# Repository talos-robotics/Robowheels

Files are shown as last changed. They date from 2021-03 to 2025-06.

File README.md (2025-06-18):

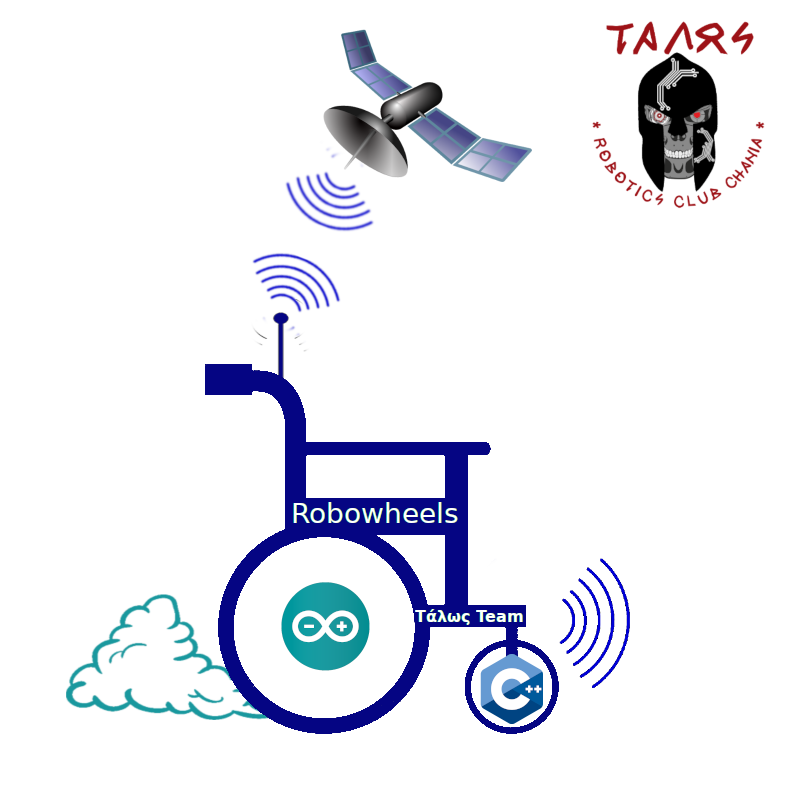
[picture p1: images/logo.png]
#   

<div style="background-color:#90EE90;">

# (The Robowheels project)

# Αυτοματοποιημένο αναπηρικό αμαξίδιο

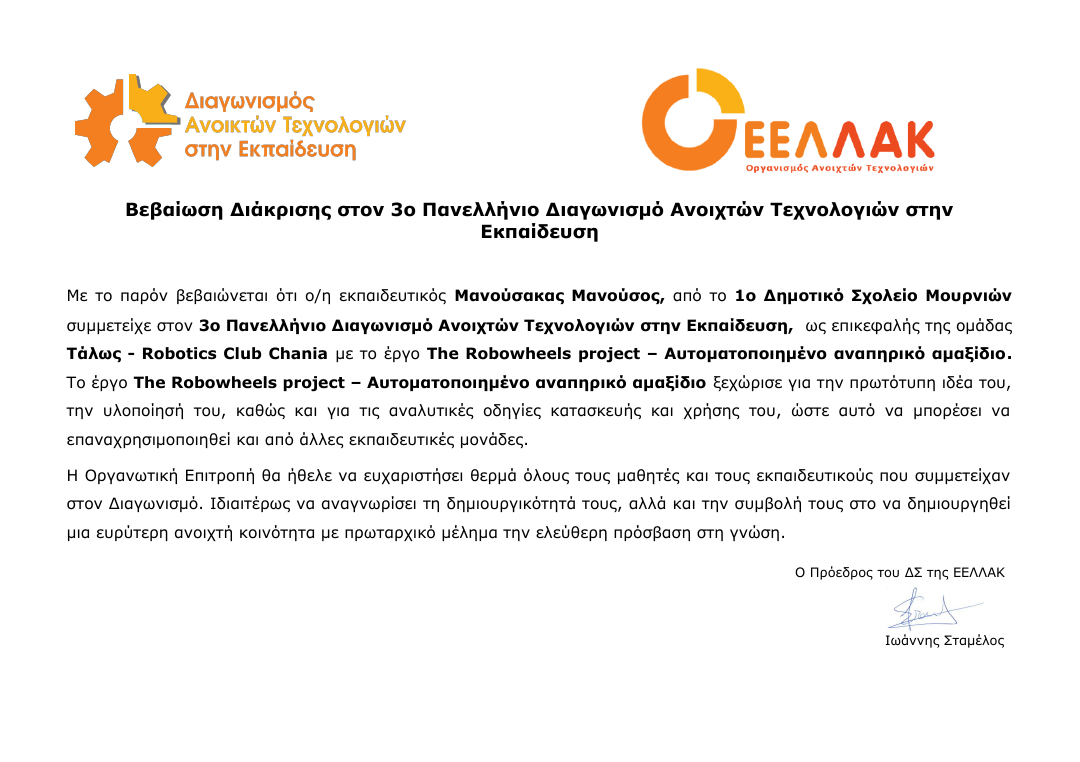
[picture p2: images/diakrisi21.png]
air


# Δημοσίευση στον τύπο
https://www.haniotika-nea.gr/ta-paidia-kainotomei/

</div>

<div style="text-align: left; ">

## <u>Συμμετέχοντες</u>

### Υπεύθυνος εκπαιδευτικός

Μανούσακας Μανούσος - Εκπαιδευτικός Πληροφορικής ΠΕ86

### Μαθητές

*   Αναστασάκης Ιωάννης
*   Ρουσιάκης Πέτρος
*   Στραβοπόδη Κωνσταντίνα

</div>

<div>

# <u>Γενικά στοιχεία σεναρίου</u>

## Σενάριο δραστηριότητας

Αριθμός μαθητών: 5  
Αριθμός Ομάδων: 2  
Αριθμός ατόμων ανά ομάδα: 2-3  
Είδος δραστηριότητας: Ομαδοσυνεργατική  
Ρόλοι: Δεν υπάρχουν διακριτοί ρόλοι στην ομάδα.  
Ηλικιακή ομάδα: 12-15  

## Φάση προετοιμασίας

Οι μαθητές θα πρέπει να:  
• Διερευνήσουν στο διαδίκτυο και να ανακαλύψουν τις ανάγκες των ατόμων με κινητικά προβλήματα.  
• Συντάξουν ένα έντυπο όπου θα περιγράφουν τις προδιαγραφές του project.  
• Να αναζητήσουν στο διαδίκτυο πληροφορίες για τους αισθητήρες που θα χρησιμοποιήσουμε.  

## Φάση σχεδιασμού

Οι μαθητές θα πρέπει να:  
• Να αναζητήσουν στο διαδίκτυο πληροφορίες για τη συνδεσμολογία των αισθητήρων με το Arduino.  
• Να αναζητήσουν στο διαδίκτυο πληροφορίες για τις προδιαγραφές των αισθητήρων.  
• Να δημιουργήσουν στο Fritzing τις παραπάνω συνδεσμολογίες.  

## Φάση υλοποίησης

Οι μαθητές θα πρέπει να:  
• Δημιουργήσουν τις φυσικές συνδέσεις των υλικών τους με τους αισθητήρες.  
• Να προγραμματίσουν το Arduino χρησιμοποιώντας το περιβάλλον Arduino IDE έτσι ώστε να παίρνουν τιμές από τους αισθητήρες.  

## Φάση Δοκιμών

Οι μαθητές θα πρέπει να:  
• Δοκιμάσουν τον εξοπλισμό τους και να επιβεβαιώσουν τη σωστή λειτουργία του.  

# Υλικά ηλεκτρονικά

<table style="width: 100%;" border="1">

<tbody>

<tr>

<th>ΠΟΣΟΤΗΤΑ</th>

<th>ΕΙΔΟΣ</th>

<th>ΚΟΣΤΟΣ</th>

<th>Σχόλια</th>

</tr>

<tr>

<td>1</td>

<td>ARDUINO UNO</td>

<td>25</td>

<td></td>

</tr>

<tr>

<td>2</td>

<td>GP2Y0A21YK0F Sharp IR Analog Distance Sensor</td>

<td>20</td>

<th>  
</th>

</tr>

<tr>

<td>1</td>

<td>Adafruit Επιταχυνσιόμετρο 3 Αξόνων ±2/4/8g @ 14-bit - MMA8451</td>

<td>8</td>

<th>  
</th>

</tr>

<tr>

<td>2</td>

<td>12V 35RPM JGY37-520 - 37mm Eccentric Large Torque Gear Motor Gearbox with Metal Gearbox</td>

<td>13</td>

<th>  
</th>

</tr>

<tr>

<td>1</td>

<td>Οδηγός για Βηματικό Κινητήρα L298N Dual H Bridge</td>

<td>4</td>

<th>  
</th>

</tr>

<tr>

<td>3</td>

<td>LM2596 Step Down Module DC 3V-40V to 5V 12V 3A Voltage Regulator</td>

<td>15</td>

<th>  
</th>

</tr>

<tr>

<td>1</td>

<td>Voice Recognition Module Rev3 Kit -Arduino Compatible</td>

<td>32</td>

<th>  
</th>

</tr>

<tr>

<td>1</td>

<td>SIM808 GPS GSM GPRS Bluetooth Module W/2.4G Antenna Replace SIM908 For Arduino</td>

<td>44</td>
<td>ΧΡΕΙΑΖΕΤΑΙ ΜΟΝΟ ΓΙΑ ΤΗΝ ΠΕΡΙΠΤΩΣΗ ΑΝΑΒΑΘΜΙΣΗΣ – ΕΠΕΚΤΑΣΗΣ. ΟΧΙ ΓΙΑ ΤΗΝ ΒΑΣΙΚΗ ΕΚΔΟΣΗ.</td>

<th>  
</th>

</tr>

<tr>

<td>2</td>

<td>Πυκνωτές >10μF</td>

<td>1</td>

<td></td>

</tr>

<tr>

<td>2</td>

<td>UPS BATTERY 12V 14AH MAX. 210A</td>

<td>20</td>

<td></td>

</tr>

<tr>

<td>  
</td>

<td>Σύνολο</td>

<td>170</td>

<th>  
</th>

</tr>

</tbody>

</table>

## Χρήσιμα αρχεία

<table style="width: 100%;" border="1">

<tbody>

<tr>

<th>ΠΕΡΙΓΡΑΦΗ</th>

<th>ΜΕΤΑΦΟΡΤΩΣΗ</th>

<th>ΣΧΟΛΙΑ</th>

</tr>

<tr>

<td>SharpIR Βιβλιοθήκη</td>

<td><a href="https://github.com/guillaume-rico/SharpIR.git">SharpIR Βιβλιοθήκη</a></td>

<td></td>

</tr>

<tr>

<td>Adafruit MMA8451 Βιβλιοθήκη</td>

<td><a href="https://github.com/adafruit/Adafruit_MMA8451_Library.git">Adafruit MMA8451 Βιβλιοθήκη</a></td>

<th>  
</th>

</tr>

<tr>

<td>Adafruit Sensor Βιβλιοθήκη</td>

<td><a href="https://github.com/adafruit/Adafruit_Sensor.git">Adafruit Sensor Βιβλιοθήκη</a></td>

<td></td>

</tr>

<tr>

<td>Voice Recognition Module οδηγός χρήσης</td>

<td><a href="images/VR3_manual.pdf">VR3_manual.pdf</a></td>

<td></td>

</tr>

<tr>

<td>Voice Recognition Module Βιβλιοθήκη</td>

<td><a href="https://www.google.com/url?q=https%3A%2F%2Fgithub.com%2Felechouse%2FVoiceRecognitionV3%2Farchive%2Fmaster.zip&sa=D&sntz=1&usg=AFQjCNE7a6-RkPLi9FMpjxIFqR-6OoMh5Q">VR3 library</a></td>

<td></td>

</tr>

<tr>

<td>L298N Βιβλιοθήκη</td>

<td><a href="https://downloads.arduino.cc/libraries/github.com/AndreaLombardo/L298N-2.0.2.zip?_gl=1*4jdbxj*_ga*MTg5MDYwNzAzMC4xNjMyNDIyNjU0*_ga_NEXN8H46L5*MTYzMjk5NjE0Mi42LjAuMTYzMjk5NjE0Mi4w">L298N</a></td>

<td></td>

</tr>

<tr>

<td></td>

<td></td>

<td></td>

</tr>

</tbody>

</table>

## Υλικά για την κατασκευή

<table style="width: 100%;" border="1">
<tbody>
<tr>
<th>ΠΟΣΟΤΗΤΑ</th>
<th>ΕΙΔΟΣ</th>
<th></th>
<th>Σχόλια</th>
</tr>
<tr>
<td style="text-align: center;">1</td>
<td>Ράβδος αλουμινίου 4cm x 2cm  Μήκος - 1m</td>
<td></td>
<td></td>
</tr>
<tr>
<td style="text-align: center;">2</td>
<td>Ράβδος αλουμινίου 4cm x 2cm  Μήκος - 40 cm</td>
<td></td>
<td></td>
</tr>
<tr>
<td style="text-align: center;">2</td>
<td>Βάση για μοτέρ 3d μοντέλο για εκτύπωση</td>
<td></td>
<td><a href="https://github.com/talos-robotics/Robowheels/blob/main/images/JGB37-520%20mount.STL">Κατεβάστε απο εδώ</a></td>
</tr>
<tr>
<td></td>
<td>Βίδες αυτοδιάτρητες  - διάφορα μεγέθη</td>
<td></td>
<td></td>
</tr>
<tr>
<td style="text-align: center;">2</td>
<td>Ασφάλειες μεταλλικές - κοπίλια</td>
<td></td>
<td></td>
</tr>
<tr>
<td style="text-align: center;">2</td>
<td>Ρόδες  με διάμετρο υποδοχής 6mm</td>
<td></td>
<td></td>
</tr>
<tr>
<td style="text-align: center;">1</td>
<td>Γωνιακό προφίλ αλουμινίου 40 cm</td>
<td></td>
<td></td>
</tr>
<tr>
<td style="text-align: center;">1</td>
<td>Μονοτική ταινία</td>
<td></td>
<td></td>
</tr>
<tr>
<td style="text-align: center;">2</td>
<td>Ράβδος αλουμινίου 4cm x 2cm  Μήκος - 20m</td>
<td></td>
<td></td>
</tr>
<tr>
<td style="text-align: center;">12</td>
<td>Βίδες Υ:2cm Π:4χιλ.</td>
<td></td>
<td></td>
</tr>
<tr>
<td style="text-align: center;"></td>
<td>Καλώδια 0.4 mm Διάφορα χρώμματα</td>
<td></td>
<td></td>
</tr>
<tr>
<td style="text-align: center;"></td>
<td>Κολλητήρι -  Καλάι</td>
<td></td>
<td></td>
</tr>
<tr>
<td style="text-align: center;"></td>
<td>Πιστόλι σιλικόνης - Ράβδοι συλικόνης</td>
<td></td>
<td></td>
</tr>
<tr>
<td style="text-align: center;"></td>
<td>Δραπανοκατσάβιδο μπαταρίας</td>
<td></td>
<td></td>
</tr>
<tr>
<td style="text-align: center;">2</td>
<td>Ροδάκια Επίπλων Περιστρεφόμενα</td>
<td></td>
<td></td>
</tr>
</tbody>
</table>

## Κατασκευή υποτιθέμενου αμαξιδίου ( εξομοιωτή )

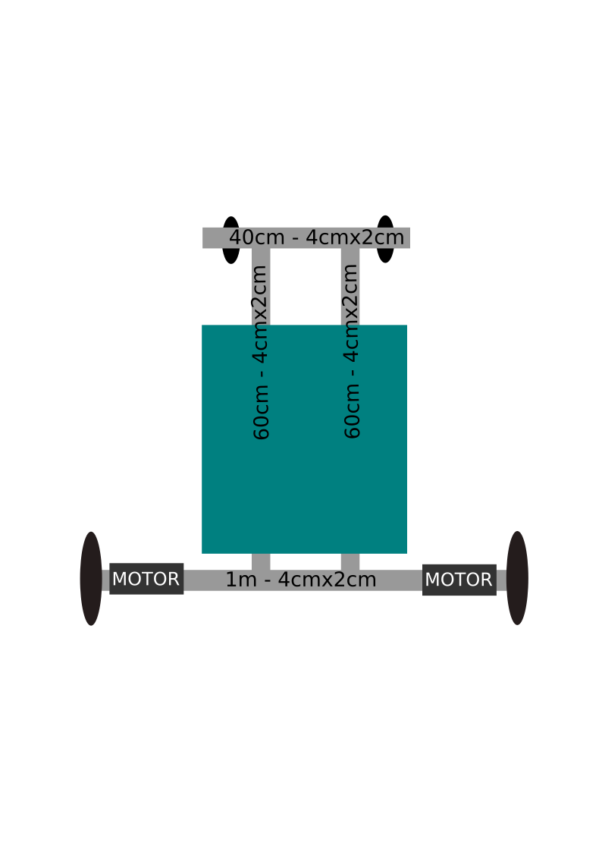
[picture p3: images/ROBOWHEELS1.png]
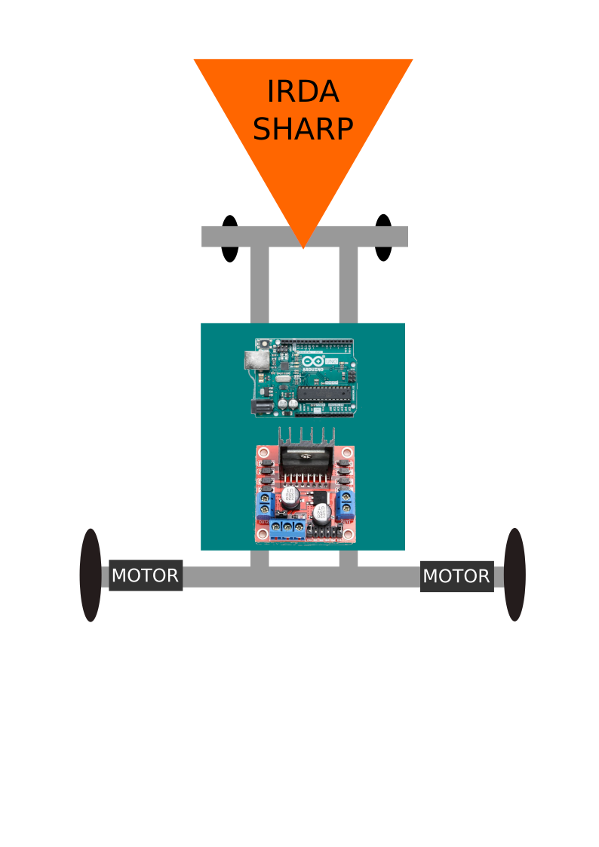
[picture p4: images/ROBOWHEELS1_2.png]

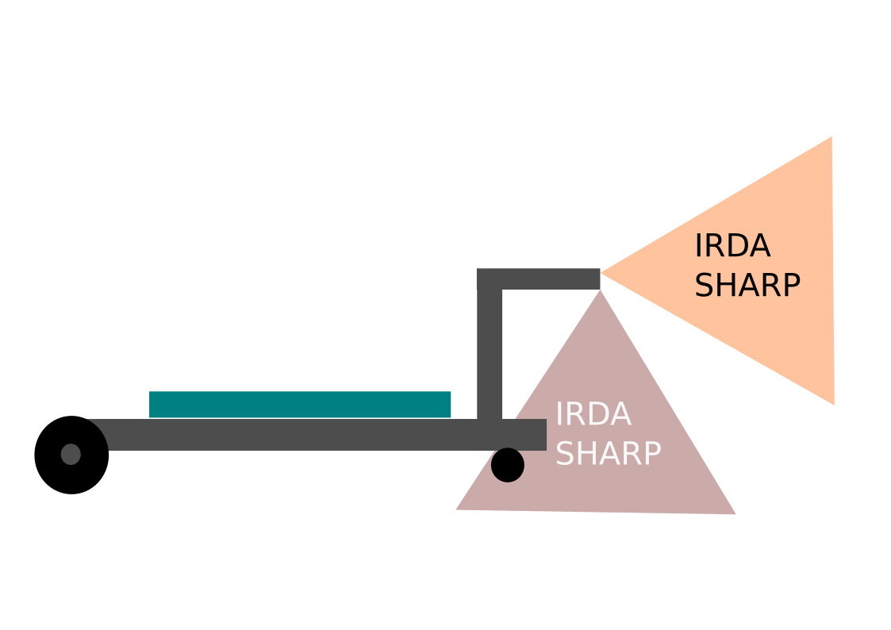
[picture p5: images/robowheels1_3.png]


## Προοπτική κατασκευής σε πραγματικό αμαξίδιο

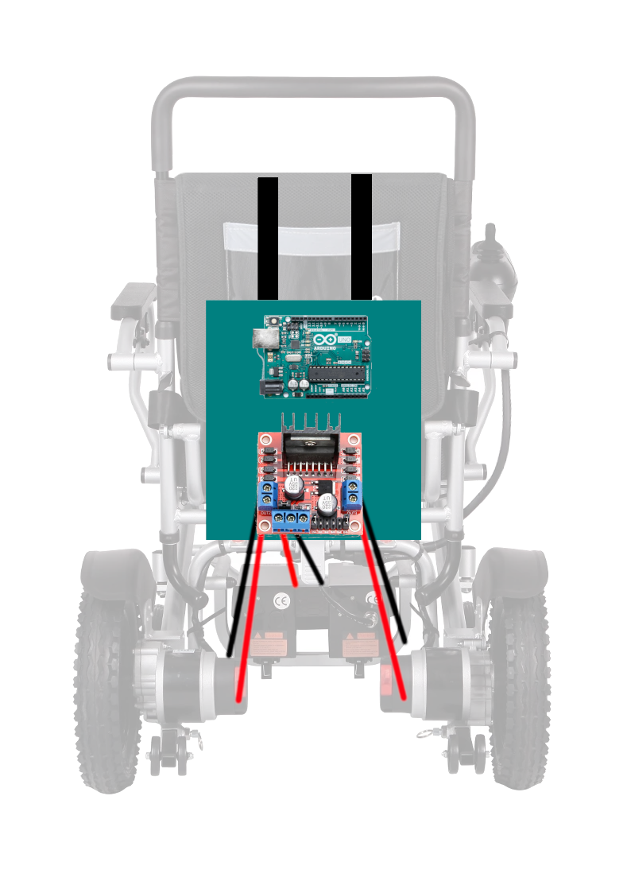
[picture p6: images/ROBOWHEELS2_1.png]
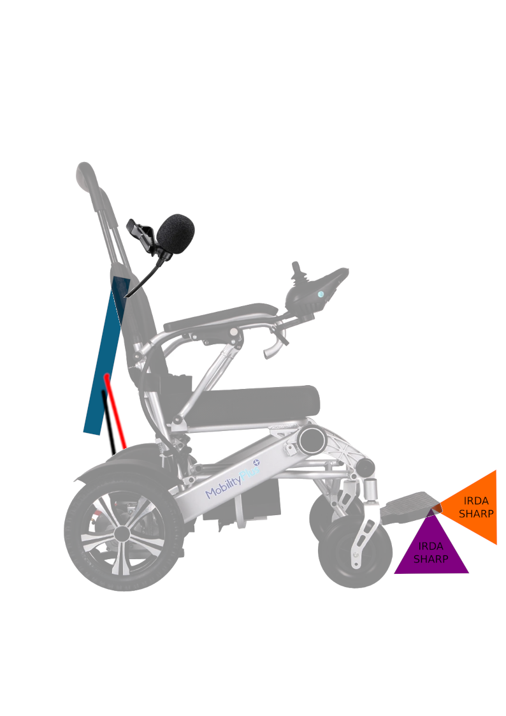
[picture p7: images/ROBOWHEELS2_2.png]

	
### <big>Αναλυτική περιγραφή</big>

Οι μαθητές αφού βρουν στοιχεία για την τετραπληγία και την παραπληγία 
θα μελετήσουν τις ανάγκες και τις λειτουργικές ικανότητες των ατόμων αυτών. 
Σκοπός είναι η δημιουργία ενός αυτοματοποιημένου οχήματος μετακίνησης που θα
προσαρμόζεται ανάλογα το μέλος του σώματος που θα είναι ικανός να θέσει σε
κίνηση ο χρήστης του. Θα παρέχει βασικές δικλείδες ασφαλείας για την ακινητοποίησή του.

<b>Ένα ηλεκτρικό αναπηρικό αμαξίδιο κοστίζει από 3000 ευρώ και πάνω. Θα ήταν αδύνατο να έχουμε στη διάθεση μας κάτι τέτοιο έτσι ώστε να το τροποποιήσουμε και να πειραματιστούμε.Άλλωστε ας μην ξεχνάμε πως ο διαγωνισμός έχει εκπαιδευτικό χαρακτήρα. Έτσι λοιπόν θα δημιουργήσουμε μια απλή κατασκευή που θα προσομοιώνει το αμαξίδιο και θα πειραματιστούμε πάνω σε αυτό. Οι αρχές λειτουργίας παραμένουν οι ίδιες.</b>
	
Ανάλογα την οικονομική και χρονική δυνατότητα που θα έχουμε, θα μπορούσε να προστεθεί 
και σύστημα εντοπισμού θέσης και επικοινωνίας που θα μπορεί να θέσει 
ο χρήστης σε λειτουργία σε περίπτωση κινδύνου.

Σκοπός και οφέλη

    • Ευαισθητοποίηση των μαθητών στο κοινωνικό θέμα της αναπηρίας.
    • Αναζήτηση λύσεων μετά από μελέτη προδιαγραφών και απαιτήσεων.
    • Εισαγωγή στην κατασκευή και λειτουργία βασικών ηλεκτρονικών κυκλωμάτων.
    • Εισαγωγή σε προγραμματιστικά περιβάλλοντα.
    • Εισαγωγή σε θέματα μηχανικής και κατασκευών.
    • Ομαδική δουλειά και συνεργασία.

</div>

<div>

# <u>Πλατφόρμες που χρησιμοποιήθηκαν</u>

Όλα τα διαδικτυακά εργαλεία που χρησιμοποιήσαμε ανήκουν στο Πανελλήνιο σχολικό δίκτυο.  

<small><small><font style="font-size: 24pt;" size="6"><small><small>**Πλατφόρμες εργασίας**</small></small></font></small></small>

<dl>

<dt><small><small><font style="font-size: 18pt;" size="5"><small><small>**Ηλεκτρονική τάξη:** https://eclass.sch.gr</small></small></font></small></small></dt>

<dt><small><small><font style="font-size: 18pt;" size="5"><small><small>**Πλατφόρμα τηλεδιασκέψεων:** cisco webex</small></small></font></small></small></dt>

<dt><small><small><font style="font-size: 18pt;" size="5"><small><small>**Ομαδοσυνεργατικά έγγραφα:** https://grafis.sch.gr</small></small></font></small></small></dt>

<dt><small><small><font style="font-size: 18pt;" size="5"><small><small>**Ηλεκτρονικό ταχυδρομείο:** https://webmail.sch.gr</small></small></font></small></small></dt>

<dt><small><small><font style="font-size: 18pt;" size="5"><small><small>**Υπηρεσία Επικοινωνίας:**</small></small></font><font style="font-size: 18pt;" size="5"><small> <small></small> </small></font><font style="font-size: 18pt;" size="5"><small><small>https://www.uc.sch.gr</small></small></font></small></small></dt>

</dl>

</div>

<div>

# <u>Εργαλεία ΕΛΛΑΚ που χρησιμοποιήθηκαν</u>

*   Libreoffice
*   Linux - Elementary OS
*   Arduino IDE
*   Fritzing

</div>

<div>

# <u>Πληροφορίες για το υλικό</u>

### Αισθητήρας GP2Y0A21 IRDA

<br />

Οι αισθητήρες απόστασης Sharp είναι μια δημοφιλής επιλογή για πολλά έργα που απαιτούν ακριβείς μετρήσεις απόστασης. 

Αυτός ο αισθητήρας υπερύθρων είναι απο τους πιο οικονομικούς, ωστόσο παρέχει πολύ καλύτερη απόδοση από άλλες εναλλακτικές λύσεις IR.
Η διασύνδεση με τους περισσότερους μικροελεγκτές είναι απλή.
Το εύρος ανίχνευσης αυτής της έκδοσης είναι περίπου 10 cm έως 80 cm (4 ″ έως 32).

Το GP2Y0A21 χρησιμοποιεί υποδοχή 3 ακίδων.Αυτά τα καλώδια έχουν συνδετήρες JST 3 ακίδων στο ένα άκρο και διατίθενται με προ-πτυχωμένες αρσενικές ακίδες,
στο άλλο άκρο. 
Είναι επίσης δυνατή η συγκόλληση τριών καλωδίων στον αισθητήρα όπου είναι τοποθετημένες οι ακίδες σύνδεσης 

	Κόκκινο --> 5V
	Μαύρο --> GND
	Κίτρινο --> DATA (Αναλογικό)

### Αισθητήρας Adafruit Επιταχυνσιόμετρο 3 Αξόνων ±2/4/8g @ 14-bit - MMA8451

<br />

Το MMA8451 είναι ένα μικροσκοπικό επιταχυνσιόμετρο από την Freescale, η οποία είναι (πλέον) αυθεντία στο παιχνίδι του σχεδιασμού επιταχυνσιόμετρων.
Έχει σχεδιαστεί για χρήση σε τηλέφωνα, tablet, έξυπνα ρολόγια και άλλα, αλλά λειτουργεί εξίσου καλά και στο έργο σας Arduino.
Από την οικογένεια MMA8451/MMA8452/MMA8453, ο MMA8451 είναι ο πιο ακριβής με ενσωματωμένο ADC 14-bit.
Το επιταχυνσιόμετρο διαθέτει επίσης ενσωματωμένη ανίχνευση κλίσης/προσανατολισμού, ώστε να μπορεί να σας πει αν το έργο σας βρίσκεται σε οριζόντια ή κατακόρυφη θέση
και αν έχει κλίση προς τα εμπρός ή προς τα πίσω.

Τυπική Τάση Εισόδου:
    3VDC
    5VDC
Ρεύμα Λειτουργίας: 165uA
Διασύνδεση:Ψηφιακή 
Πρωτόκολλο Eπικοινωνίας:I2C

 **Αρχή λειτουργίας επιταχυνσιόμετρου.**

IMAGE ALT TEXT HERE (https://www.youtube.com/embed/To7JagpPDwY)

### Κινητήρας dc 12V 35RPM JGY37-520 - 37mm Eccentric Large Torque Gear Motor Gearbox with Metal Gearbox



Οι Κινητήρες DC είναι συνεχείς ενεργοποιητές που μετατρέπουν την ηλεκτρική ενέργεια σε μηχανική ενέργεια. Ο κινητήρας DC επιτυγχάνει αυτό με τη δημιουργία μιας συνεχούς γωνιακής περιστροφής που μπορεί να χρησιμοποιηθεί για την περιστροφή αντλιών, ανεμιστήρων, συμπιεστών, τροχών κλπ. Ο κινητήρας DC ή κινητήρας συνεχούς ρεύματος για να του δώσουμε τον πλήρη τίτλο του είναι ο συνηθέστερα χρησιμοποιούμενος κινητήρας για την παραγωγή συνεχούς κίνηση και της οποίας η ταχύτητα περιστροφής μπορεί εύκολα να ελεγχθεί, καθιστώντας τους ιδανικά για χρήση σε διάφορες εφαρμογές. Ένας ηλεκτροκινητήρας συνεχούς ρεύματος αποτελείται από δύο μέρη, έναν "στάτορα" που είναι το σταθερό τμήμα και έναν "περιστροφέα" που είναι το περιστρεφόμενο τμήμα. Οι κινητήρες DC έχουν σχεδόν γραμμικά χαρακτηριστικά με την ταχύτητα περιστροφής τους να καθορίζεται από την εφαρμοζόμενη τάση συνεχούς ρεύματος και η ροπή εξόδου τους να καθορίζεται από το ρεύμα που ρέει μέσω των περιελίξεων του κινητήρα. Η ταχύτητα περιστροφής κάθε κινητήρα DC μπορεί να ποικίλει από μερικές περιστροφές ανά λεπτό (σ.α.λ.) σε πολλές χιλιάδες στροφές ανά λεπτό, καθιστώντας τις κατάλληλες για ηλεκτρονικές, αυτοκινητοβιομηχανικές ή ρομποτικές εφαρμογές. Συνδυάζοντας τους με κιβώτια ταχυτήτων (Gearbox), η ταχύτητα εξόδου τους μπορεί να μειωθεί, ενώ παράλληλα αυξάνει την ισχύ ροπής του κινητήρα σε υψηλή ταχύτητα.

### Οδηγός για Βηματικό Κινητήρα L298N Dual H Bridge



Το L298N είναι ένας οδηγός για κινητήρες συνεχούς ρεύματος. Με αυτό το πλακετάκι μπορείς να δώσεις κίνηση στους κινητήρες σου, υποστηρίζει έως δύο κινητήρες μέγιστης ισχύς 2A ανά κινητήρα. Μικρός σε μέγεθος για εφαρμογή σε πλήθος κατασκευών, διαθέτει κλέμες για την σύνδεση των κινητήρων και του ρεύματος. Έχεις την δυνατότητα να το χρησιμοποιήσεις και σε μεγαλύτερο εύρος εφαρμογών εκτός από κινητήρες, όπως ρελέ, solenoids, DC ή Stepper κινητήρες.

ΧΑΡΑΚΤΗΡΙΣΤΙΚΑ
Max. Current per Channel: 2A
Τύπος Οδηγού: DC Motor Stepper

ΕΠΙΠΛΕΟΝ ΧΑΡΑΚΤΗΡΙΣΤΙΚΑ

Driver: L298N Dual H Bridge DC Motor Driver IC
Motor Power Supply Vs: +5 V to +35 V
Max average current: 2A
Peak current Io: 3A
Logic Level Power Vss: +5 V ~ +7 V (Onboard 5V Regulator can be used if Motor Power is > 7.0V)
Logic level power: 0 - 36mA
Logic signal input range: [ Low:-0.3V ≤ Vin ≤ 1.5V] [ High: 2.3V ≤ Vin ≤ Vss]
Maximum power dissipation: 20W (when the temperature T = 75 ℃)

### Μετατροπέας DC-DC Step-Down 1.3-35V 3A



Πρόκειται για ένα DC Adjustable Step Down Module που μπορεί να χρησιμοποιηθεί 
για την επίτευξη εύρους ρυθμιζόμενης τάσης εξόδου 1.3V-35V με βάση το LM2596S.
Περιλαμβάνει LC Ripple Filtering για ομαλότερη τάση εξόδου.

ΧΑΡΑΚΤΗΡΙΣΤΙΚΑ
Τάση Εισόδου: 3.2-40Volt
Τάση Εξόδου: 1.3-35Volt
Ένταση Εξόδου: 3Amp
ΕΠΙΠΛΕΟΝ ΧΑΡΑΚΤΗΡΙΣΤΙΚΑ

    Input voltage 3.2V - 40V
    Output voltage 1.3V - 35V
    Output current 3A (max)
    Conversion efficiency of 92% (maximum)
    Output ripple <30mV
    Switching frequency 65KHz
    Operating temperature -45 ℃ ~ +85 ℃

### Αισθητήρας Αναγνώρισης Φωνής



Το Voice Recognition Module είναι μια εύχρηστη μονάδα αναγνώρισης ομιλίας που μπορεί εύκολα να διασυνδεθεί με το Arduino.
Υποστηρίζει συνολικά έως και 80 φωνητικές εντολές.
Μέγιστες 7 φωνητικές εντολές θα μπορούσαν να λειτουργήσουν ταυτόχρονα. Κάθε ήχος θα μπορούσε να εκπαιδευτεί ως εντολή.
Οι χρήστες πρέπει πρώτα να εκπαιδεύσουν τη μονάδα πριν την αφήσουν να αναγνωρίσει οποιαδήποτε φωνητική εντολή.

ΧΑΡΑΚΤΗΡΙΣΤΙΚΑ
Τύπος Αισθητήρα:

    Ήχου

Τυπική Τάση Εισόδου:

    5VDC
    5.5VDC

Ρεύμα Λειτουργίας: 40mA
Διασύνδεση:

    Ψηφιακή 

Πρωτόκολλο Eπικοινωνίας:

    UART

ΕΠΙΠΛΕΟΝ ΧΑΡΑΚΤΗΡΙΣΤΙΚΑ

    Voltage: 4.5-5.5V
    Current: <40mA
    Digital Interface: 5V TTL level for UART interface and GPIO
    Analog Interface: 3.5mm mono-channel microphone connector + microphone pin interface
    Recognition accuracy: 99% (under ideal environment)

### Waveshare GSM/GPRS/GPS Shield SIM808 - Χρειάζεται μόνο για την περίπτωση αναβάθμισης - επέκτασης. Όχι για αυτή την βασική έκδοση. Θα δημιουργηθεί σαν ξεχωριστό project στο μέλλον



Το GSM/GPRS/GPS Shield (B) είναι μια ασπίδα Arduino που βασίζεται στη μονάδα τεσσάρων ζωνών GSM/GPRS/GPS SIM808.

ΧΑΡΑΚΤΗΡΙΣΤΙΚΑ
Τυπος Shield:

    GPRS/GSM
    GPS

ΕΠΙΠΛΕΟΝ ΧΑΡΑΚΤΗΡΙΣΤΙΚΑ

    Arduino connectivity, compatible with UNO, Leonardo, NUCLEO, XNUCLEO
    Onboard USB TO UART converter CP2102 for UART debugging
    5 x LEDs for indicating the module working status
    Onboard voltage level converter, supports both 3.3V and 5V systems
    SIM card slot for 1.8V/3V SIM card
    Baudrate auto detection (1200bps ~115200bps)
    Bluetooth 3.0， supports data transferring through Bluetooth
    RTC with power supply interface
    Firmware upgradable via USB
    Control via AT commands (3GPP TS 27.007,27.005, and SIMCOM enhanced AT Commands)
    Supports SIM application toolkit: GSM 11.14 Release 99
    Operating voltage: 6 ~ 12V
    Operation temperature: -40 °C ~ +85 °C
    Storage temperature: -45 °C ~ +90 °C

ΔΥΝΑΤΟΤΗΤΕΣ

GSM/GPRS

    Band
        GSM 850/EGSM 900/DCS 1800/PCS 1900 MHz
        Quad-band auto search
        Compliant to GSM phase 2/2+
    Emitting power
        Class 4 (2W @ GSM 850/EGSM 900 MHz)
        Class 1 (1W @ DCS 1800/PCS 1900 MHz)
    GPRS connectivity
        GPRS multi-slot class 12 (default)
        GPRS multi-slot class 1~12 (configurable)
    GPRS data feature
        Downlink speed: max 85.6kbps
        Uplink speed: max 85.6kbps
        Coding schemes: CS-1\CS-2\CS-3\CS-4
        Supports PAP (Password Authentication Protocol) for PPP connection
        Embedded TCP/IP protocol
        Supports PBCCH
        Supports CSD transmission speed: 2.4/4.8/9.6/14.4 kbps
        Supports USSD
    SMS
        Supports: MT/MO/CB/Text/PDU mode
        SMS storage: SIM card
    Audio
        Voice encode/decode mode: Half Rate\Full Rate\Enhanced Full Rate\Adaptive muti rate
        Supports echo cancellation
        Supports noise reduction

GPS

    Receiver type
        22 tracking channels
        66 acquisition channels
        GPS L1 C/A code
    Sensitivity
        Tracking: -165 dBm
        Cold starts : -148 dBm
    Time-To-First-Fix
        Cold starts : 30s (typ.)
        Hot starts : < 1s
        Warm starts: 28s
    Accuracy
        Horizontal position : <2.5m CEP

</div>

<div style="text-align: center; text-decoration:">

# Συνδεσμολογία Υλικού

<div style="text-align: left; font-size: 12pt; background-color:yellow">

**<u>ΠΕΡΙΓΡΑΦΗ ΛΕΙΤΟΥΡΓΙΑΣ - Με τη χρήση ΜΜΑ8451</u>**

Στη συγκεκριμένη εκδοχή χρησιμοποιούμε ένα γυροσκοπικό αισθητήρα τον οποίο τον προσαρμόζουμε στο μέλος του σώματος που μπορεί το άτομο με τετραπληγία να κινήσει. Ανάλογα την κλήση που δέχεται ο γυροσκοπικός αισθητήρας από τον χρήστη εκτελεί τις αντίστοιχες κινήσεις. Όταν τον γείρει μπροστά τα μοτέρ εκτελούν εμπρόσθια κίνηση. Όταν τον γείρει πίσω τα μοτέρ εκτελούν κίνηση προς τα πίσω. Αντίστοιχα όταν τον γείρει δεξιά ή αριστερά τα μοτέρ εκτελούν τις αντίστοιχες κινήσεις.

Αυτός ο τρόπος έχει σημαντικά πλεονεκτήματα. Ένας άνθρωπος με κινητικές δυσκολίες μπορεί να έχει πολλές ιδιαιτερότητες στο μέλος του σώματος που θα θέτει το όχημα σε κίνηση.
Για παράδειγμα αν περιστρέφει τον αισθητήρα με το κεφάλι του, η κίνηση που κάνει δεξιά ίσως είναι μικρότερη της κίνησης που κάνει αριστερά, Με αυτό τον αισθητήρα μπορούμε να ρυθμίσουμε την ευαισθησία της κάθε κίνησης κατά το δοκούν.

</div>

#### Κατεβάστε τον κώδικα

<a href="/files/robowheelsDC.ino">Κώδικας με τον αισθητήρα MMA8451</a>

</div>

<div style="text-align: center; text-decoration:">

<div style="text-align: left; font-size: 12pt; background-color:yellow">

**<u>ΠΕΡΙΓΡΑΦΗ ΛΕΙΤΟΥΡΓΙΑΣ - Με τη χρήση Αναγνώρισης φωνής</u>**

Στη συγκεκριμένη εκδοχή χρησιμοποιούμε μία μονάδα αναγνώρισης φωνής και με φωνητικές εντολές, οι οποίες
έχουν προγραμματιστεί εκ των προτέρων, μπορεί να θέσει σε κίνηση ο χρήστης τα μοτέρ.
Για παράδειγμα θα μπορούσε να πει τη λέξη μπροστά και τα μοτέρ να εκτελέσουν εμπρόσθια κίνηση.
Θα μπορούσε να πει τη λέξη δεξιά και τα μοτέρ να εκτελέσουν δεξιά στροφή.
Θα μπορούσε να πει την λέξη stop για να μπορέσει να τερματίσει τη λειτουργία του μοτέρ.
Ένα πλεονέκτημα της συγκεκριμένης μονάδας αναγνώρισης φωνής, είναι ότι είναι ανεξάρτητη γλώσσας και χροιάς.
Μπορεί και συγκρίνει τους φθόγγους με αυτό που έχουμε καταγράψει αρχικά. 
Επίσης κάποιοι συνάνθρωποί μας με δυσκολία στην ομιλία ίσως μπορούν να προφέρουν μόνο ήχους. Είναι σε θέση η μονάδα αυτή να τους κατανοήσει. 
Μια πολύ θετική παράμετρος.
Ενα βασικό μειονέκτημα της πολύ σημαντικό είναι ότι επηρεάζεται αρνητικά από τους περιβάλλοντες ήχους με
αποτέλεσμα να μην μπορεί να γίνει σωστά η αναγνώριση.

<a href="/files/robowheels_voiceDC.ino">Κώδικας με τον αισθητήρα voice</a>
	
</div>

#### Συνδεσμολογία

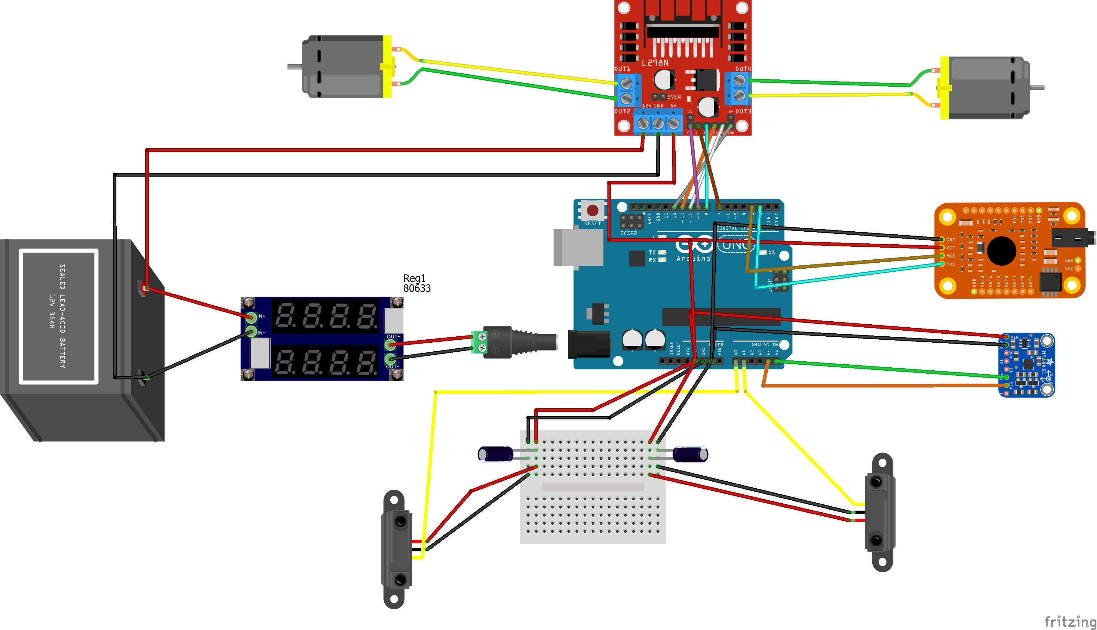
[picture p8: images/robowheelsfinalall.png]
  

#### Εκπαιδεύστε το module σας

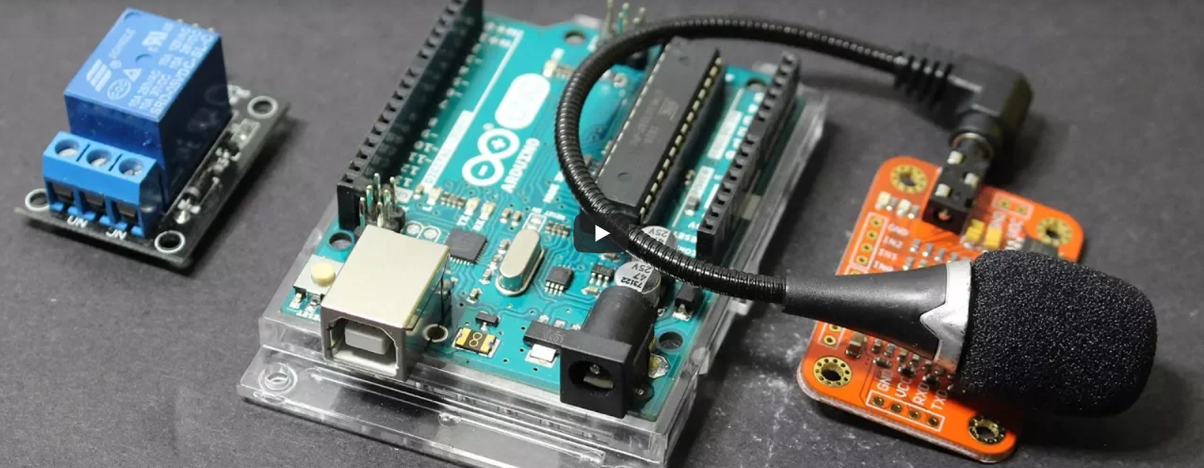
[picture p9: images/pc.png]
IMAGE ALT TEXT HERE (https://www.youtube.com/embed/bTrv1nv3oSA)


</div>

<div>

# <u><center>Στάδια εξέλιξης - Τελικό πρωτότυπο</center></u>

## Βίντεο - Παρουσίαση
IMAGE ALT TEXT HERE (https://www.youtube.com/embed/V4w2R3GzmRQ)

## Φωτογραφίες
<table style="width: 100%;" border="1">
<tbody>
<tr align="center">
<td></td>
<td></td>
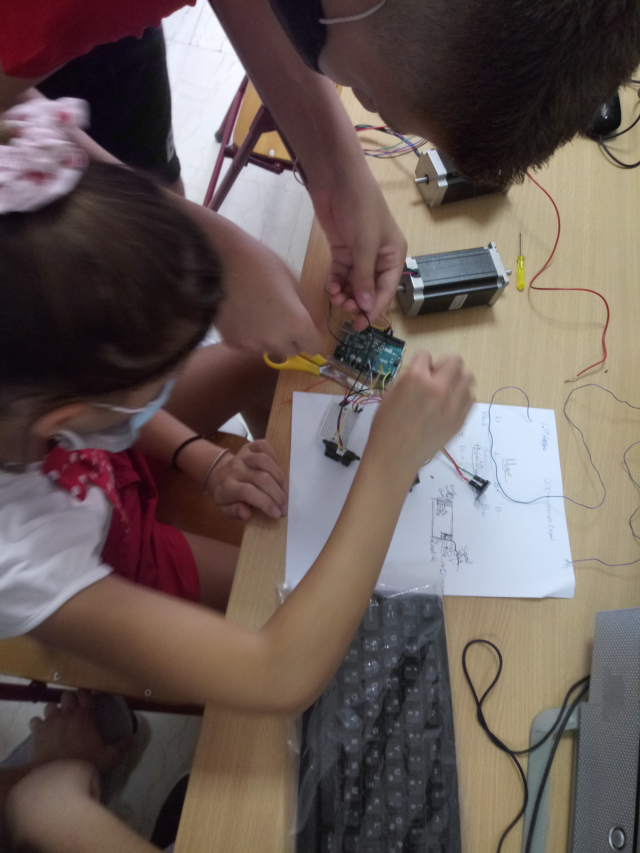
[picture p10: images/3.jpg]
<td></td>
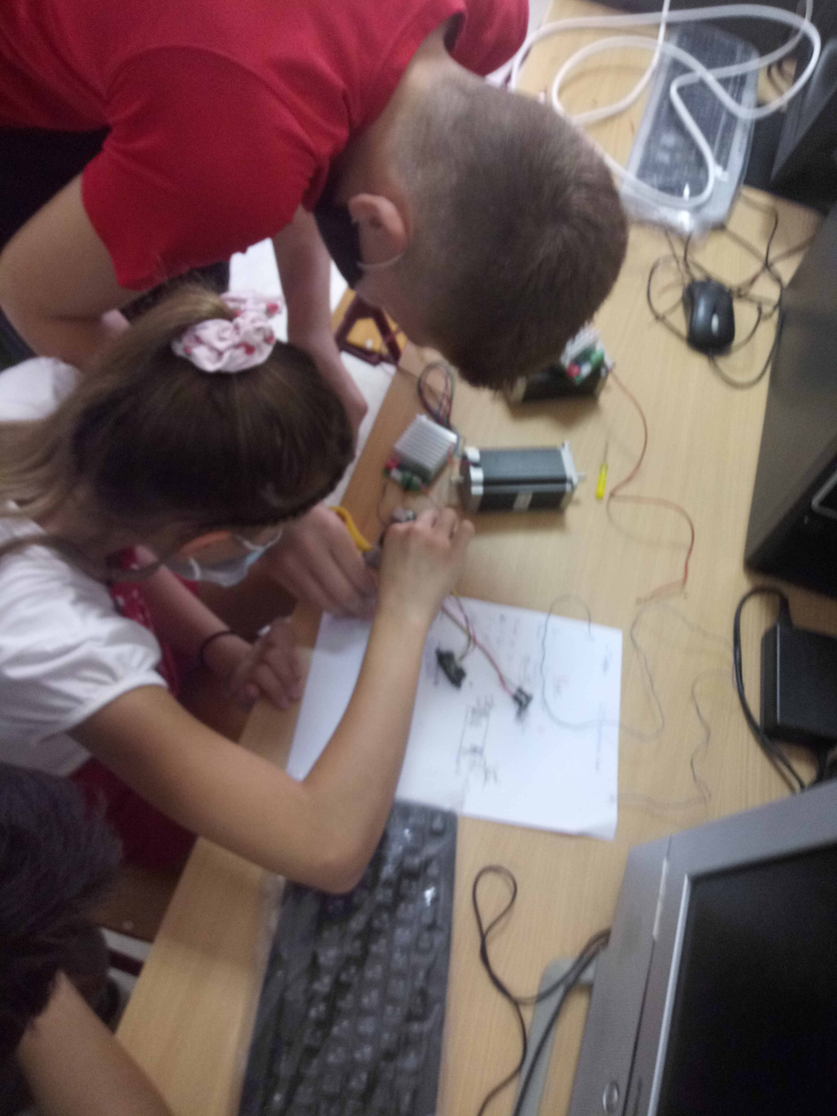
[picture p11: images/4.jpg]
<td></td>
</tr>
<tr align="center">
<td></td>
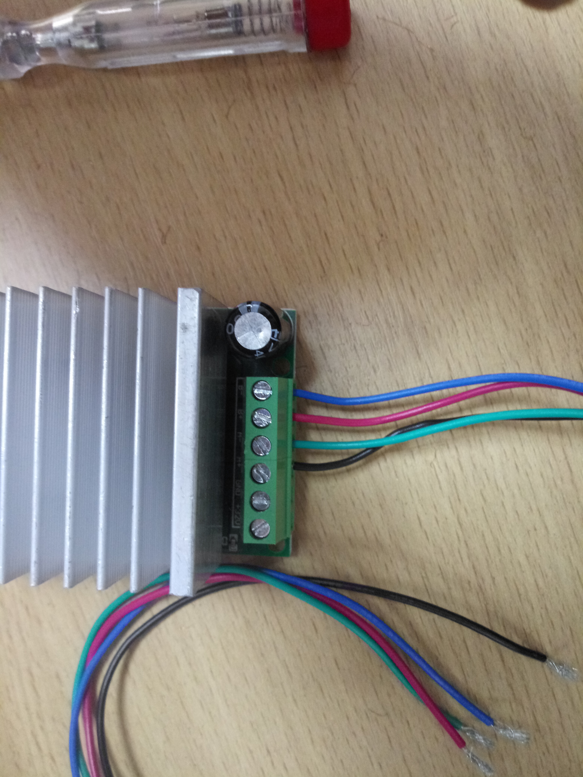
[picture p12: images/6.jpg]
<td></td>
<td></td>
<td></td>
</tr>
<tr align="center">
<td></td>
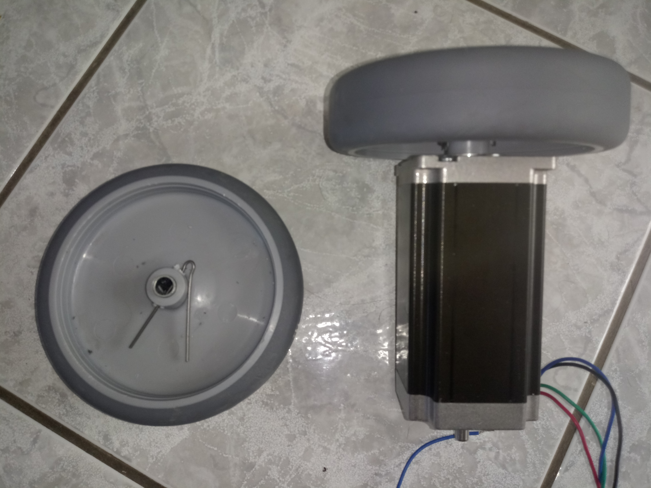
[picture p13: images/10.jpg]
<td></td>
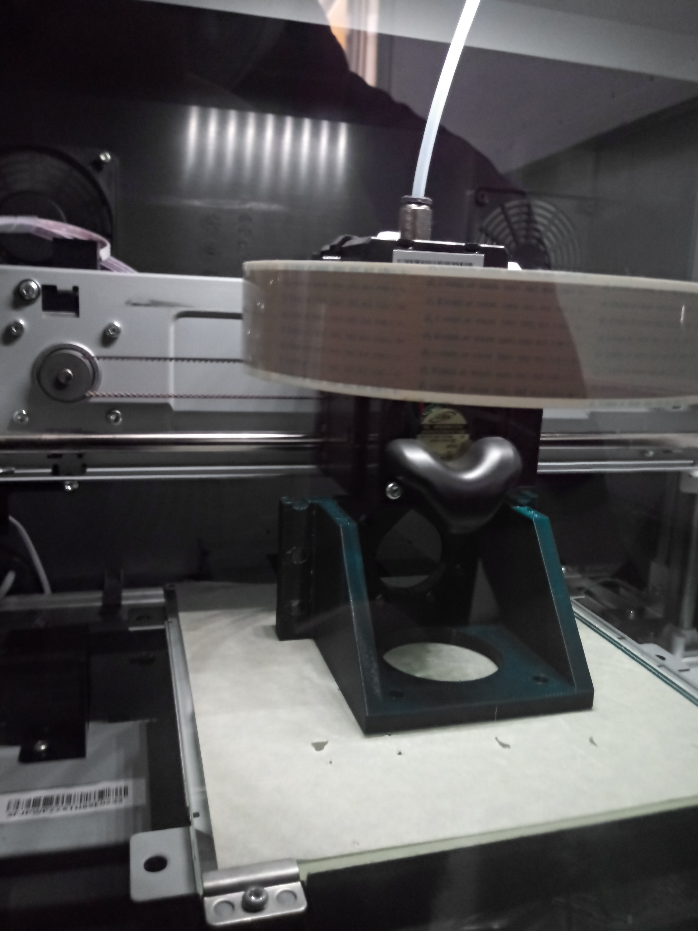
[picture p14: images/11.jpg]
<td></td>
<td></td>
</tr>
<tr align="center">
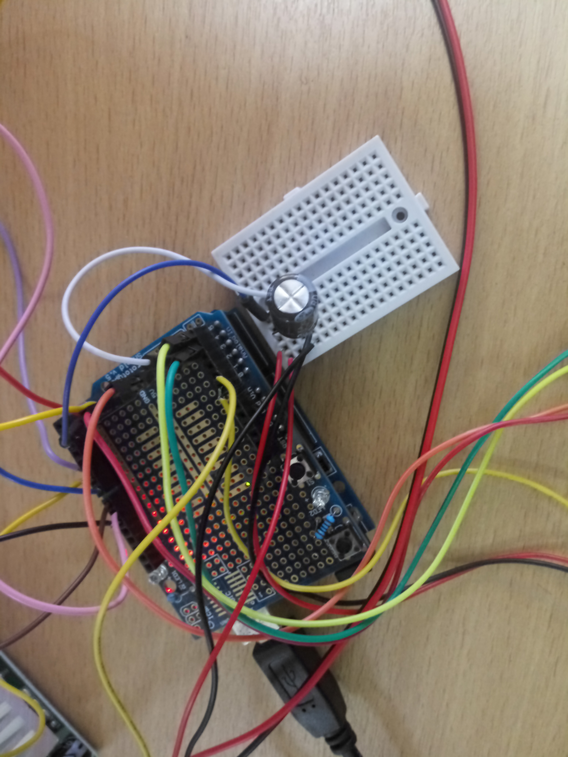
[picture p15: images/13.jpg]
<td></td>
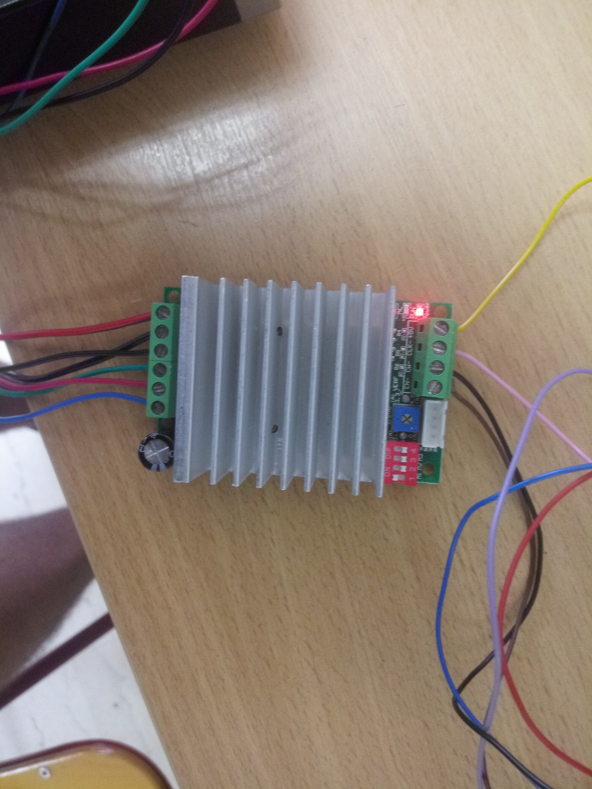
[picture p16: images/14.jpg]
<td></td>
<td></td>
<td></td>
</tr>
<tr align="center">
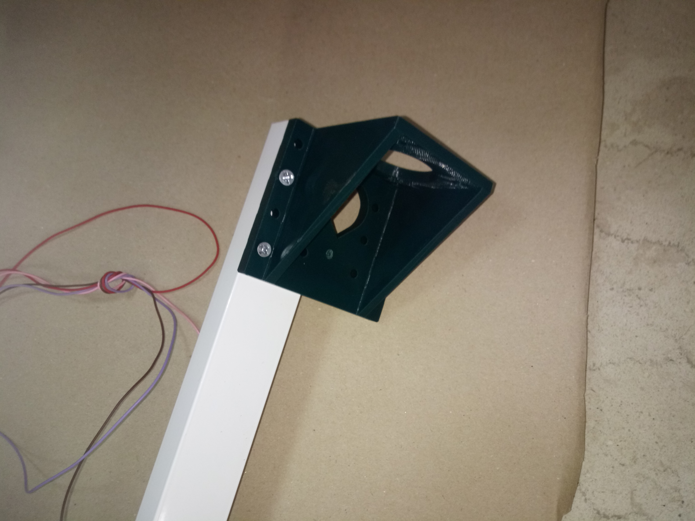
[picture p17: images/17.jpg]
<td></td>
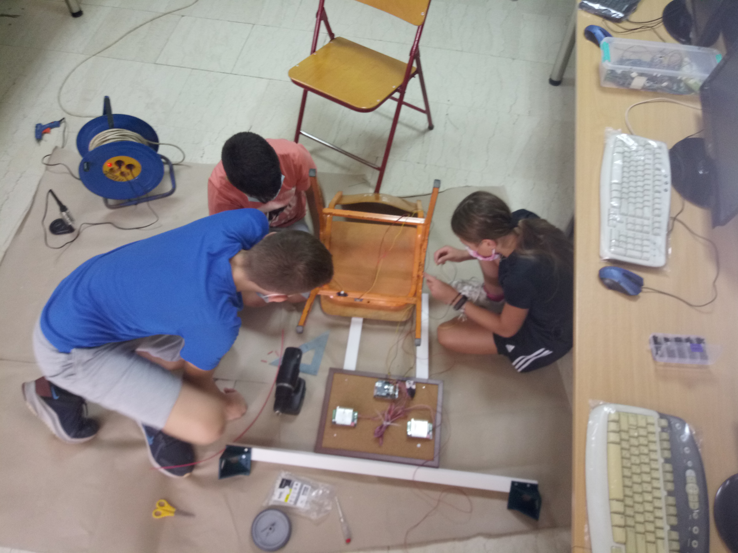
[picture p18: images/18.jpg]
<td></td>
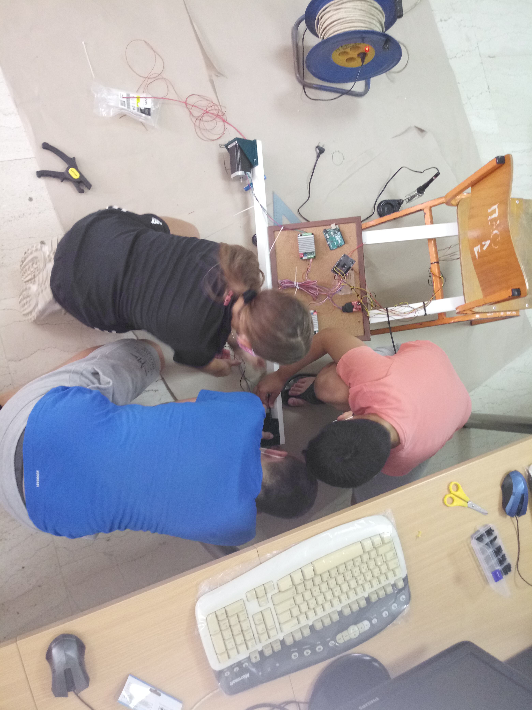
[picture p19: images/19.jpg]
<td></td>
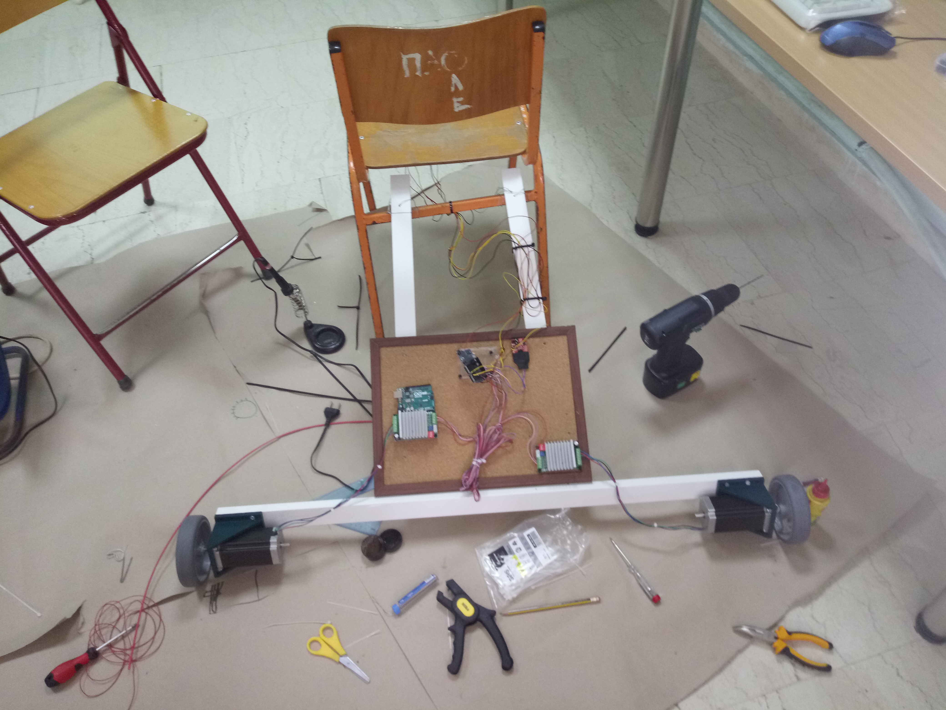
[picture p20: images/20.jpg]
<td></td>
</tr>
<tr align="center">
<td></td>
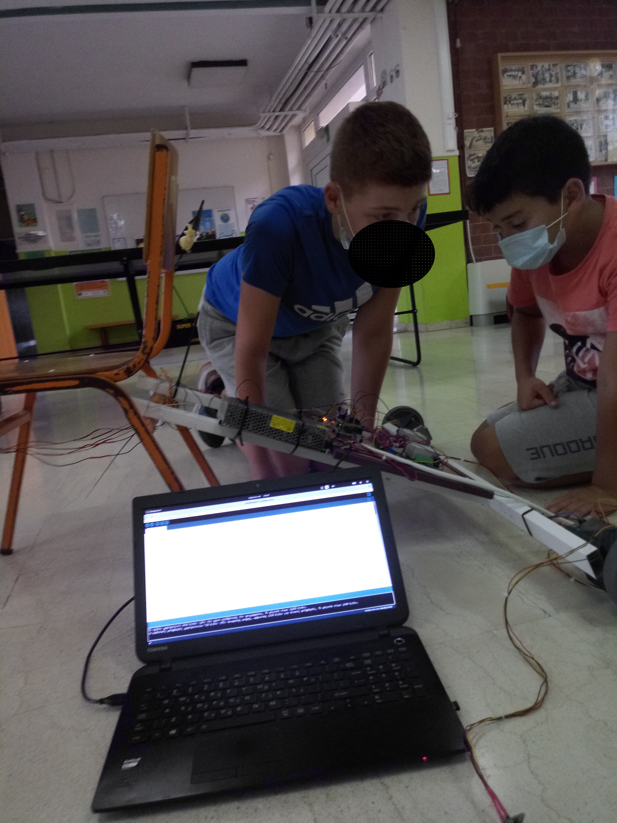
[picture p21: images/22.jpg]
<td></td>
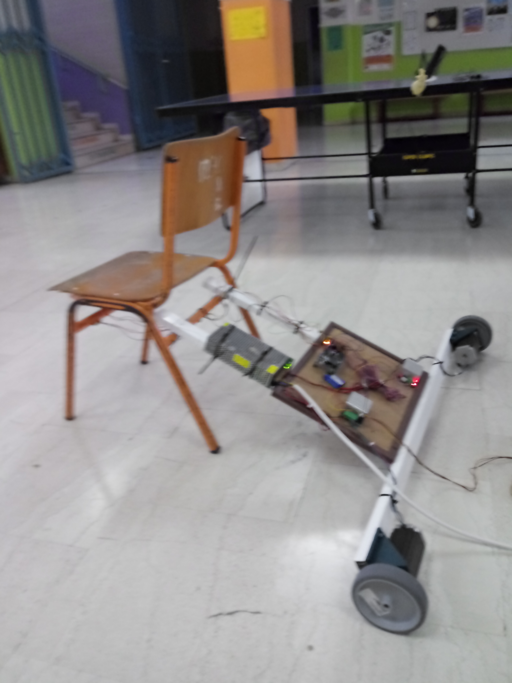
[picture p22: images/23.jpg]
<td></td>
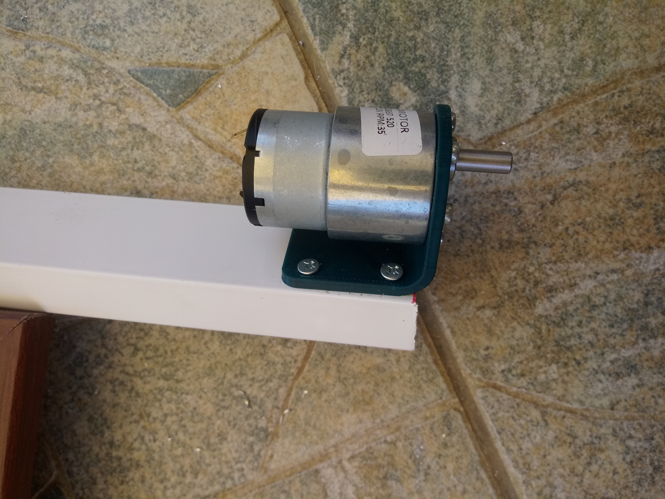
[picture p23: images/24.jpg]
<td></td>
</tr>
<tr align="center">
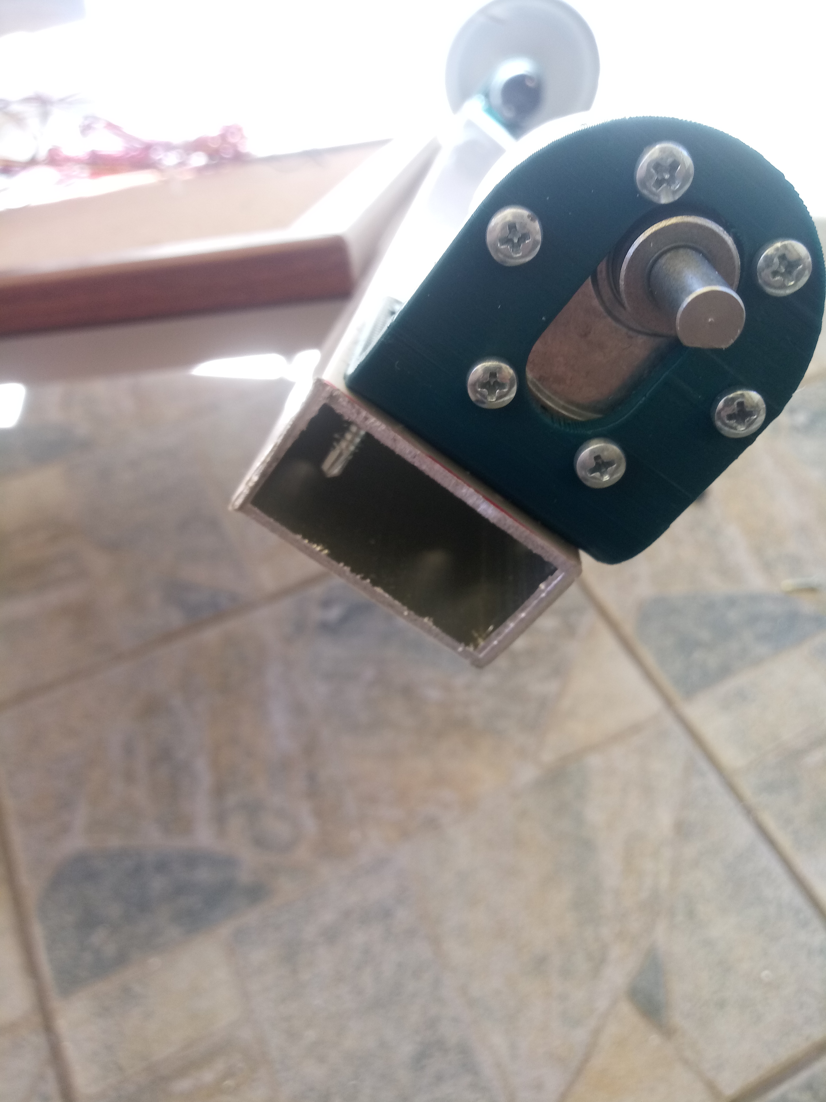
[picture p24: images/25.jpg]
<td></td>
<td></td>
<td></td>
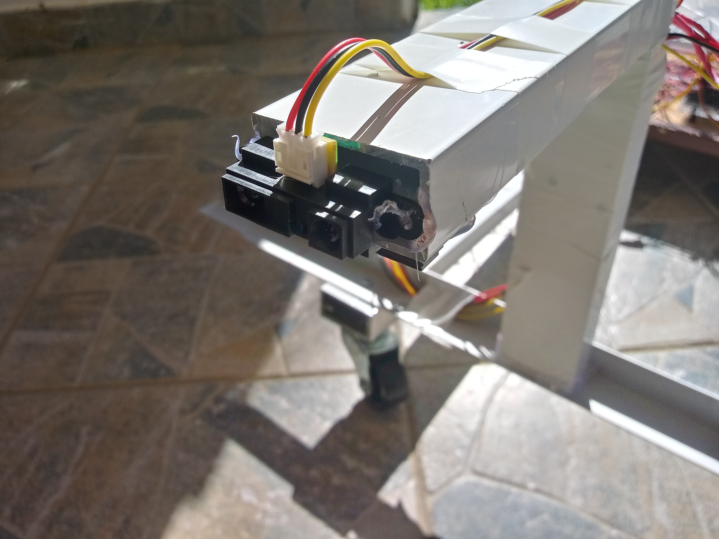
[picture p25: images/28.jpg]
<td></td>
</tr>
<tr align="center">
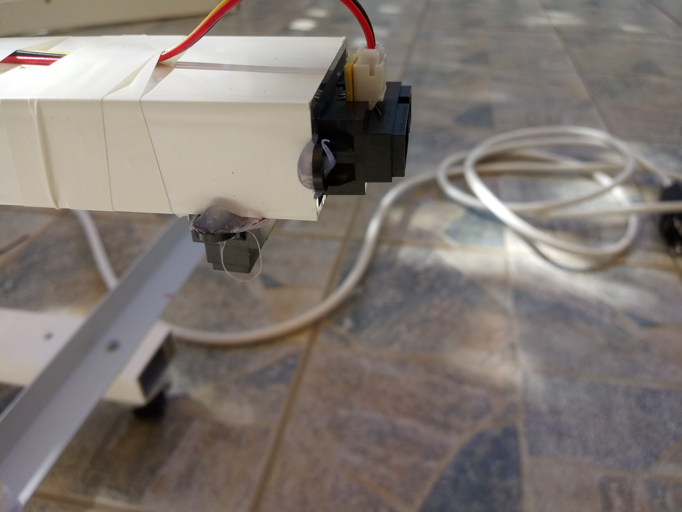
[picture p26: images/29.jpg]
<td></td>
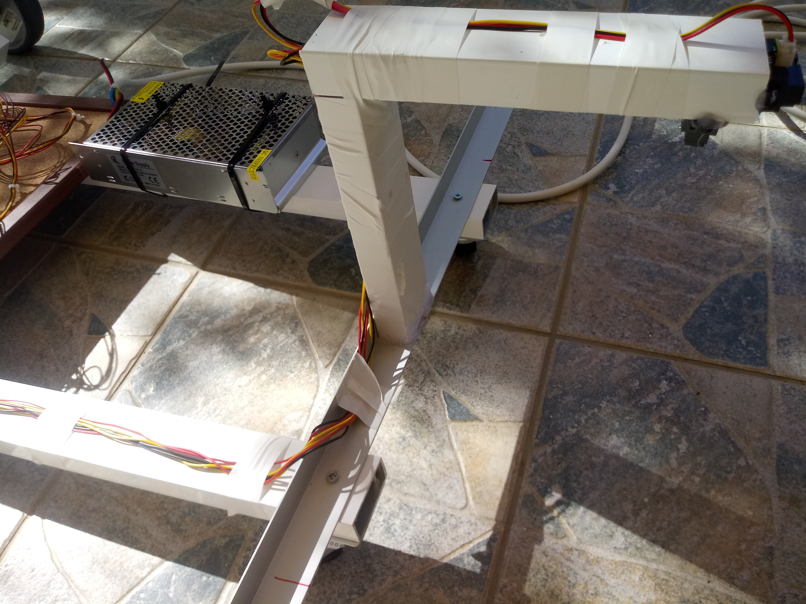
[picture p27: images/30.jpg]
<td></td>
<td></td>
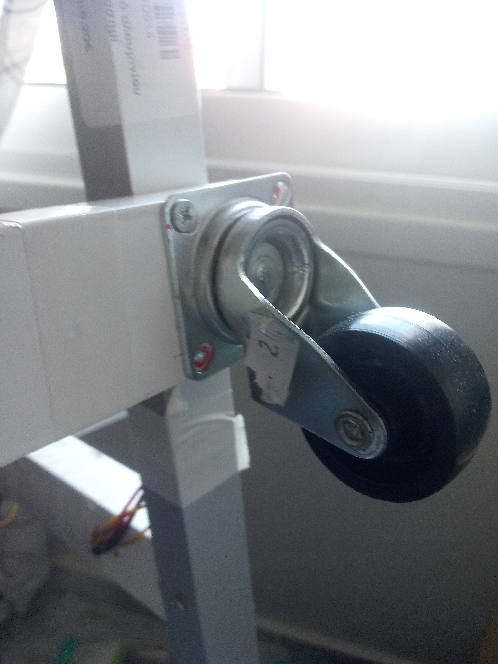
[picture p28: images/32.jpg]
<td></td>
</tr>
<tr align="center">
<td></td>
<td></td>
<td></td>
<td></td>
</tr>
</tbody>
</table>
</div>

<div>

# <u><center>Τελικά συμπερασματα</center></u>

### Γενικά

Το παρόν project ολοκληρώθηκε με επιτυχία. Οι μαθητές πέτυχαν τους γνωστικούς στόχους και ενεπλάκησαν ενεργά σε γνωστικούς πυλώνες όπως η Επιστήμη, η Τεχνολογία, η Μηχανική και τα Μαθηματικά – STEM. Προγραμματιστικά οι μαθητές απέδωσαν τα μέγιστα για την ηλικιακή τους ομάδα. Κατανόησαν πλήρως τις προγραμματιστικές δομές, που είχαν κατακτήσει γνωστικά μέσα στην τάξη με γλώσσες προγραμματισμού εκπαιδευτικού τύπου, και τις χρησιμοποίησαν σε γλώσσα προγραμματισμού υψηλού επιπέδου. Κατανόησαν σε μεγάλο βαθμό την έννοια του αντικειμένου και του αντικειμενοστραφούς προγραμματισμού.

Όπως σε κάθε πρωτότυπο έτσι κι εδώ αντιμετωπίσαμε μερικές δυσλειτουργίες. Τις δυσλειτουργίες αυτές τις καταγράψαμε, τις αναφέρουμε και δώσουμε λύσεις παρακάτω.

Προγραμματιστικά το πρωτότυπο κρίνεται άρτιο , ολοκληρωμένο και λειτουργικό..

### Δυσλειτουργίες - Αστοχίες
	
1. Η επιλογή των βηματικών μοτέρ ήταν κακή επιλογή. Τα μοτέρ αυτά έχουν σημαντικά μειονεκτήματα. Έχουν πολύ χαμηλή ταχύτητα και μειονεκτούν σε ροπή. Στα επιλεγμένα μοτέρ η ροπή ήταν πολύ καλή αλλά η ταχύτητα ήταν πάρα πολύ αργή.
Ένα άλλο μειονέκτημα των μοτέρ αυτών είναι η συνεχής κατανάλωση ρεύματος ακόμα και όταν δεν λειτουργούν.
Τέλος ανεβάζουν υπερβολικές θερμοκρασίες &gt;100 oC. Αυτό είχε σαν αποτέλεσμα μετά από μερικές ώρες λειτουργίας οι βάσεις στήριξης των μοτέρ που ήταν κατασκευασμένες σε τρισδιάστατο εκτυπωτή με υλικό PLA να λιώσουν στα σημεία επαφής. Αυτό σημαίνει ότι τα μοτέρ ξεπέρασαν τους 170 oC που είναι και το σημείο τήξης του PLA.

2. Η μονάδα φωνητικής αναγνώρισης μειονεκτεί σε περιβάλλον θορύβου, και δυσκολεύεται να καταλαβαίνει τις φωνητικές εντολές.

### Λύσεις – Προτάσεις (αντίστοιχα)
	
1. Η επιλογή δύο DC μοτέρ είναι επιβεβλημένη. Η επιλογή πρέπει να γίνει με γνώμονα την ταχύτητα σε σχέση με την ροπή. Γενικά όσο μεγαλώνει η ταχύτητα η ροπή μικραίνει.

Δείτε τα σχετικό βίντεο παρακάτω.
	
<b>Λίγη φυσική</b>

Αν υποθέσουμε οτι το μοτερ εχει ροπή 60 kg-cm. Η ροπή αυτή αναφέρεται στη διαθέσιμη ροπή στον άξονα του κινητήρα.
Αν κάποιος τοποθετήσει μια τροχαλία ακτίνας R και σηκώσει βάρος W, τότε ανάλογα με την ακτίνα της τροχαλίας, το βάρος που μπορεί να σηκωθεί θα ποικίλει, αλλά το γινόμενο της ακτίνας της τροχαλίας R και της βάρος W που μπορεί να ανυψωθεί θα είναι σταθερό και ίσο με τη ροπή που αναπτύσσει ο κινητήρας. Στην περίπτωσή μας εξετάζουμε δύο παραδείγματα, το ένα με τροχαλία ακτίνας 1 cm και το άλλο με ακτίνα 2 cm. Δεδομένου ότι η διαθέσιμη ροπή είναι 60 kg cm, τα βάρη που μπορούν να σηκωθούν είναι 60 kg και 30 kg αντίστοιχα.

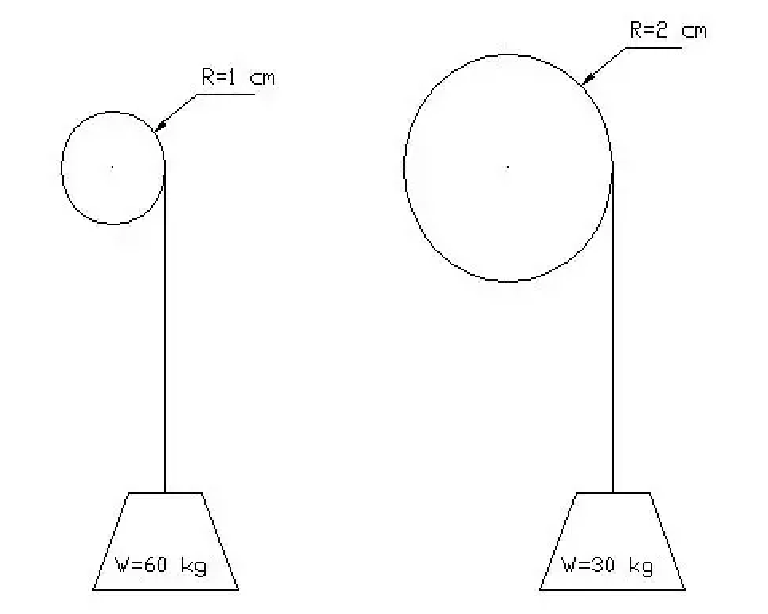
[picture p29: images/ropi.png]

	
<b>Bίντεο 1</b>
(https://www.youtube.com/embed/UUfZnZ_0Cb8)
	
<b>Bίντεο 2</b>
(https://www.youtube.com/embed/5IjG4iSJYQ4)	
	
Πρέπει να βρεθεί μια χρυσή τομή μεταξύ των δύο παραμέτρων.

Κάποιες προτάσεις μοτέρ παρακάτω
	
https://www.cableworks.gr/ilektronika/arduino-and-microcontrollers/motors/dc/12v-35rpm-jgy37-520-37mm-eccentric-large-torque-gear-motor-gearbox-with-metal-gearbox/

https://www.hellasdigital.gr/electronics/motors-and-drivers/dc/metal-dc-geared-motor-12v-50rpm-50kg.cm-fit0492-a/

2. Θα ήταν καλό να χρησιμοποιηθεί μια ποιοτικότερη μονάδα αναγνώρισης φωνής με επιλογή ευαισθησίας του μικροφώνου.

</div>

<p style="text-align: center;"></br>
Αυτή η εργασία χορηγείται με άδεια <a href="http://creativecommons.org/licenses/by-sa/4.0/" rel="license">Creative Commons Αναφορά Δημιουργού - Παρόμοια Διανομή 4.0 Διεθνές </a>.</p>

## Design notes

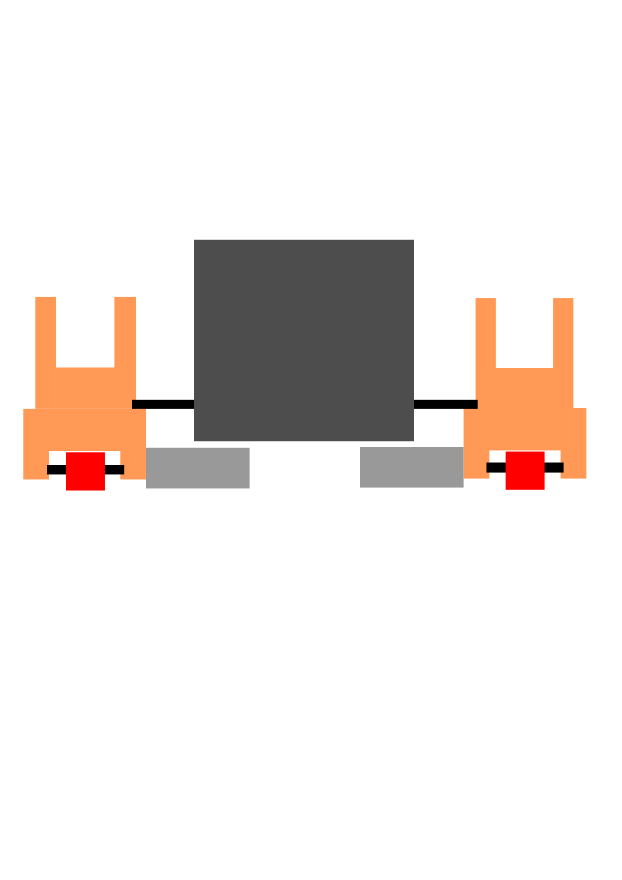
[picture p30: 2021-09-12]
images/back.png

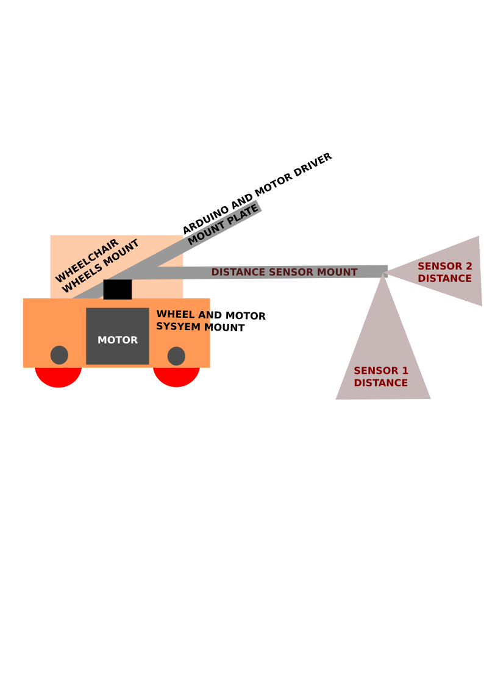
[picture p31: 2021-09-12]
images/side.png

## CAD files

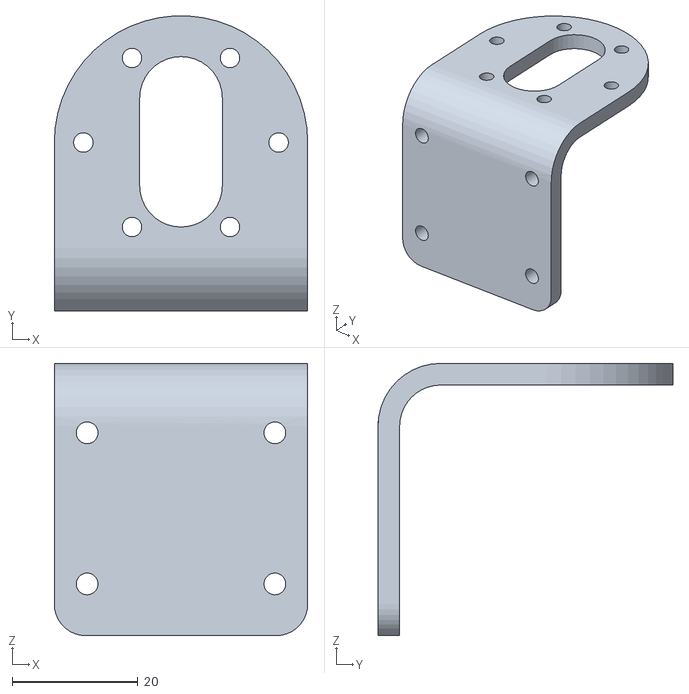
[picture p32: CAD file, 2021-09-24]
images/JGB37-520 mount.STL
40.4 x 47.0 x 43.4

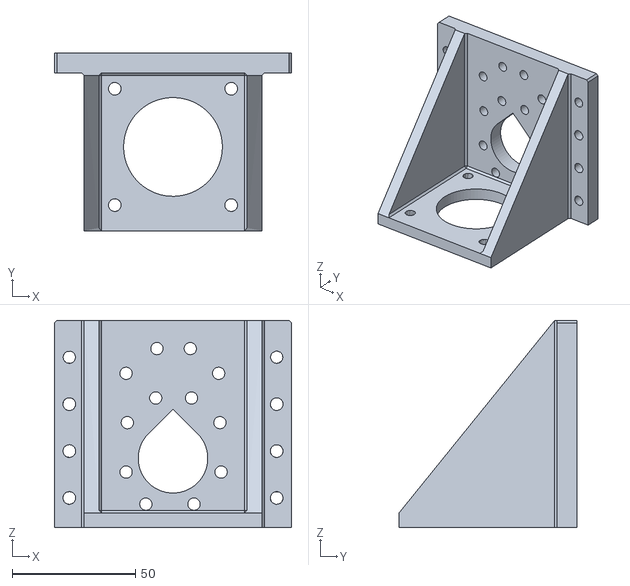
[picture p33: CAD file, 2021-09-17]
images/mountmodel.stl
96.0 x 72.0 x 83.9

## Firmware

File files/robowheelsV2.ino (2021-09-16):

 
#include <SharpIR.h>
#include <Wire.h>
#include <Adafruit_MMA8451.h>
#include <Adafruit_Sensor.h>

// ΜΕΤΑΒΛΗΤΕΣ ΓΙΑ ΤΟ ΑΡΙΣΤΕΡΟ ΜΟΤΕΡ
byte directionPin = 10;
byte stepPin = 9;
byte enablePin = 8;
int numberOfSteps = 20;
int millisbetweenSteps = 0;

//ΜΕΤΑΒΛΗΤΕΣ ΓΙΑ ΤΟ ΔΕΞΙ ΜΟΤΕΡ
byte directionPin_R = 7;
byte stepPin_R = 6;
byte enablePin_R = 5;
int numberOfSteps_R = 20;

int distance1;
int distance2;

SharpIR sensor1 ( SharpIR:: GP2Y0A21YK0F, A0);
SharpIR sensor2 ( SharpIR:: GP2Y0A21YK0F, A1);

Adafruit_MMA8451 mma = Adafruit_MMA8451();

void setup() {

Serial.begin(9600);

//ΑΡΧΙΚΟΠΙΟΙΣΗ ΚΑΙ ΕΝΕΡΓΟΠΙΟΙΣΗ PINS ΑΡΙΣΤΕΡΟΥ ΜΟΤΕΡ
pinMode(directionPin, OUTPUT);
pinMode(stepPin, OUTPUT);
pinMode(enablePin, OUTPUT);

digitalWrite(enablePin, HIGH);
digitalWrite(directionPin, HIGH);

//ΑΡΧΙΚΟΠΙΟΙΣΗ ΚΑΙ ΕΝΕΡΓΟΠΙΟΙΣΗ PINS ΔΕΞΙΟΥ ΜΟΤΕΡ
pinMode(directionPin_R, OUTPUT);
pinMode(stepPin_R, OUTPUT);
pinMode(enablePin_R, OUTPUT);

digitalWrite(enablePin_R, HIGH);
digitalWrite(directionPin_R, HIGH);
delay(100);


 Serial.println("Adafruit MMA8451 test!");
  

  if (! mma.begin()) {
    Serial.println("Couldnt start");
    while (1);
  }
  Serial.println("MMA8451 found!");
  

}


void loop() {

// Διαβαζουμε τις τιμες του αισθητηρα mma8451
   mma.read();
  Serial.print("X:\t"); Serial.print(mma.x); 
  Serial.print("\tY:\t"); Serial.print(mma.y); 
  Serial.println();

 distance1 = sensor1.getDistance();
 distance2 = sensor2.getDistance();

Serial.print(distance1);
Serial.print(" , ");
Serial.println(distance2);
 

// ελεγχουμε τις συνθηκες για να παει το μοτερ μπροστα
 
if (distance1 >= 40 and distance2 <= 15 && mma.y >= 1800) {
Serial.print("ΜΟΤΕΡ 1 ON");
digitalWrite(directionPin_R, LOW);
digitalWrite(directionPin, HIGH);

do
{

Serial.print("ΜΟΤΕΡ 1 ON ΜΠΡΟΣΤΑ");
digitalWrite(stepPin, HIGH);
digitalWrite(stepPin, LOW);
digitalWrite(stepPin_R, HIGH);
digitalWrite(stepPin_R, LOW);
//delay(millisbetweenSteps);
mma.read();
 distance1 = sensor1.getDistance();
 distance2 = sensor2.getDistance();
}while(distance1 < 40 and distance2 > 15 && mma.y < 1800);
 
 //delay(1); 

}

// ελεγχουμε τις συνθηκες για να παει το μοτερ πισω
if (distance1 >= 40 and distance2 <= 15 && mma.y <= -1800) {
Serial.print(numberOfSteps);

digitalWrite(directionPin_R, HIGH);
digitalWrite(directionPin, LOW);

do
{

Serial.print("ΜΟΤΕΡ 1 ON πισω");
digitalWrite(stepPin, HIGH);
digitalWrite(stepPin, LOW);
digitalWrite(stepPin_R, HIGH);
digitalWrite(stepPin_R, LOW);
//delay(millisbetweenSteps);
mma.read();
 distance1 = sensor1.getDistance();
 distance2 = sensor2.getDistance();
}while(distance1 > 40 and distance2 > 15 && mma.y > -1800);
 //delay(1); 

}
//ελεγχουμε τις συνθηκες για να στριξει το μοτερ δεξια
if (distance1 >= 40 and distance2 <= 15 && mma.x >= 1400) {
Serial.print(numberOfSteps);

digitalWrite(directionPin_R, HIGH);
digitalWrite(directionPin, HIGH);

do
{

Serial.print("ΜΟΤΕΡ 1 ON δεξια");
digitalWrite(stepPin, HIGH);
digitalWrite(stepPin, LOW);
digitalWrite(stepPin_R, HIGH);
digitalWrite(stepPin_R, LOW);
//delay(millisbetweenSteps);
mma.read();
 distance1 = sensor1.getDistance();
 distance2 = sensor2.getDistance();
}while(distance1 < 40 and distance2 > 15 && mma.x < 1400);
 //delay(1); 

}

// ελεγχουμε τις συνθηκες για να παει το μοτερ αριστερα
if (distance1 >= 40 and distance2 <= 15 && mma.x <= -1400) {
Serial.print(numberOfSteps);

digitalWrite(directionPin_R, LOW);
digitalWrite(directionPin, LOW);

do
{

Serial.print("ΜΟΤΕΡ 1 ON αριστερα");
digitalWrite(stepPin, HIGH);
digitalWrite(stepPin, LOW);
digitalWrite(stepPin_R, HIGH);
digitalWrite(stepPin_R, LOW);
//delay(millisbetweenSteps);
mma.read();
 distance1 = sensor1.getDistance();
 distance2 = sensor2.getDistance();
}while(distance1 < 40 and distance2 > 15 && mma.x > -1400);
 
 //delay(1); 

}

//Σε περιπτωση αδιεξοδου
if (distance1 < 40 or distance2 > 15) {

digitalWrite(directionPin_R, HIGH);
digitalWrite(directionPin, HIGH);

do
{

Serial.println("ΜΟΤΕΡ 1 ON δεξια αδιεξοδο");
digitalWrite(stepPin, HIGH);
digitalWrite(stepPin, LOW);
digitalWrite(stepPin_R, HIGH);
digitalWrite(stepPin_R, LOW);
//delay(millisbetweenSteps);
 distance1 = sensor1.getDistance();
 distance2 = sensor2.getDistance();
}while(distance1 < 40 or distance2 > 15);
 //delay(1); 

}




}

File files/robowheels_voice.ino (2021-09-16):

#include <SoftwareSerial.h>
#include "VoiceRecognitionV3.h"
#include <SharpIR.h>
#include <Wire.h>

// ΜΕΤΑΒΛΗΤΕΣ ΓΙΑ ΤΟ ΑΡΙΣΤΕΡΟ ΜΟΤΕΡ
byte directionPin = 10;
byte stepPin = 9;
byte enablePin = 8;
int numberOfSteps = 20;
int millisbetweenSteps = 0;

//ΜΕΤΑΒΛΗΤΕΣ ΓΙΑ ΤΟ ΔΕΞΙ ΜΟΤΕΡ
byte directionPin_R = 4;
byte stepPin_R = 6;
byte enablePin_R = 5;
int numberOfSteps_R = 20;

int distance1;
int distance2;

SharpIR sensor1 ( SharpIR:: GP2Y0A21YK0F, A0);
SharpIR sensor2 ( SharpIR:: GP2Y0A21YK0F, A1);



/**        
  Connection
  Arduino    VoiceRecognitionModule
   2   ------->     TX
   3   ------->     RX
*/
VR myVR(2,3);    // 2:RX 3:TX, you can choose your favourite pins.

uint8_t records[7]; // save record
uint8_t buf[64];


int ret2;

#define mp    (0)
#define pi    (1)
#define de    (2)
#define ar    (3)
#define st    (4)  

/**
  @brief   Print signature, if the character is invisible, 
           print hexible value instead.
  @param   buf     --> command length
           len     --> number of parameters
*/
void printSignature(uint8_t *buf, int len)
{
  int i;
  for(i=0; i<len; i++){
    if(buf[i]>0x19 && buf[i]<0x7F){
      Serial.write(buf[i]);
    }
    else{
      Serial.print("[");
      Serial.print(buf[i], HEX);
      Serial.print("]");
    }
  }
}


void setup()
{
  /** initialize */
  myVR.begin(9600);
  
  Serial.begin(115200);

//ΑΡΧΙΚΟΠΙΟΙΣΗ ΚΑΙ ΕΝΕΡΓΟΠΙΟΙΣΗ PINS ΑΡΙΣΤΕΡΟΥ ΜΟΤΕΡ
pinMode(directionPin, OUTPUT);
pinMode(stepPin, OUTPUT);
pinMode(enablePin, OUTPUT);

digitalWrite(enablePin, HIGH);
digitalWrite(directionPin, HIGH);

//ΑΡΧΙΚΟΠΙΟΙΣΗ ΚΑΙ ΕΝΕΡΓΟΠΙΟΙΣΗ PINS ΔΕΞΙΟΥ ΜΟΤΕΡ
pinMode(directionPin_R, OUTPUT);
pinMode(stepPin_R, OUTPUT);
pinMode(enablePin_R, OUTPUT);

digitalWrite(enablePin_R, HIGH);
digitalWrite(directionPin_R, HIGH);
delay(100);


   
 Serial.println("Elechouse Voice Recognition V3 Module\r\nControl LED sample");
  

    
  if(myVR.clear() == 0){
    Serial.println("Recognizer cleared.");
  }else{
    Serial.println("Not find VoiceRecognitionModule.");
    Serial.println("Please check connection and restart Arduino.");
    while(1);
  }
  
  if(myVR.load((uint8_t)mp) >= 0){
    Serial.println("mprosta");
  }
  
  if(myVR.load((uint8_t)pi) >= 0){
    Serial.println("opisthen");
  }

   if(myVR.load((uint8_t)de) >= 0){
    Serial.println("ena");
  }

   if(myVR.load((uint8_t)ar) >= 0){
    Serial.println("dio");
  }

   if(myVR.load((uint8_t)st) >= 0){
    Serial.println("stop");
  }
}

void loop()
{

 distance1 = sensor1.getDistance();
 distance2 = sensor2.getDistance();

if (distance1 >= 40 and distance2 <= 20)
{

}
  int ret;
  ret = myVR.recognize(buf, 50);
  if(ret>0){
    switch(buf[1]){
      case mp:{
        Serial.println("pao mprosta ");
        Serial.println(String(buf[1]));
        Serial.println(myVR.recognize(buf, 50));
        Serial.print(distance1);
        Serial.print(" , ");
        Serial.print(distance2);
        Serial.print(" *** ");
        if (distance1 >= 40 and distance2 <= 20) {
        Serial.println("ΜΟΤΕΡ 1 ON");
        digitalWrite(directionPin_R, LOW);
        digitalWrite(directionPin, HIGH);
        ret2 =0;
        int flag = 0;
        while(distance1 >= 40 and distance2 <= 20 and flag == 0)
        {
        Serial.println("ΜΟΤΕΡ 1 ON ΜΠΡΟΣΤΑ" + String(flag));
        digitalWrite(stepPin, HIGH);
        digitalWrite(stepPin, LOW);
        digitalWrite(stepPin_R, HIGH);
        digitalWrite(stepPin_R, LOW);
         ret2 = myVR.recognize(buf, 50);
        
         Serial.println("ret2=" + String(ret2));
         
          if (ret2>0 and buf[1]>3){
           flag=1;
           Serial.println("****************************************************");
          }
       
              
        distance1 = sensor1.getDistance();
        distance2 = sensor2.getDistance();
        }
 
          

        }
       
        break;
      }
      case pi:{
      
        Serial.println("pao piso");
        Serial.println(buf[1]);
        Serial.println(myVR.recognize(buf, 50));

        digitalWrite(directionPin_R, HIGH);
        digitalWrite(directionPin, LOW);
        ret2 =0;
        int flag = 0;
        while(flag == 0)
        {
        Serial.println("ΜΟΤΕΡ 1 ON πισω" + String(flag));
        digitalWrite(stepPin, HIGH);
        digitalWrite(stepPin, LOW);
        digitalWrite(stepPin_R, HIGH);
        digitalWrite(stepPin_R, LOW);
         ret2 = myVR.recognize(buf, 50);
      
         Serial.println("ret2=" + String(ret2));
          
          if (ret2>0 and buf[1]>3){
           flag=1;
           Serial.println("****************************************************");
          }
       
              
        distance1 = sensor1.getDistance();
        distance2 = sensor2.getDistance();
        }
        
        break;
    }
        case de:{
       
        Serial.println("pao deksia");
        Serial.println(buf[1]);
        Serial.println(myVR.recognize(buf, 50));

        digitalWrite(directionPin_R, HIGH);
        digitalWrite(directionPin, HIGH);
        ret2 =0;
        int flag = 0;
        while(flag == 0)
        {
        Serial.println("ΜΟΤΕΡ 1 ON δεξια" + String(flag));
        digitalWrite(stepPin, HIGH);
        digitalWrite(stepPin, LOW);
        digitalWrite(stepPin_R, HIGH);
        digitalWrite(stepPin_R, LOW);
         ret2 = myVR.recognize(buf, 50);
        
         Serial.println("ret2=" + String(ret2));
          
          if (ret2>0 and buf[1]>3){
           flag=1;
           Serial.println("****************************************************");
          }
       
              
        distance1 = sensor1.getDistance();
        distance2 = sensor2.getDistance();
        }
        
        break;
    }
        case ar:{
       
        Serial.println("pao aristera");
        Serial.println(buf[1]);
        Serial.println(myVR.recognize(buf, 50));

        digitalWrite(directionPin_R, LOW);
        digitalWrite(directionPin, LOW);
        ret2 =0;
        int flag = 0;
        while(flag == 0)
        {
        Serial.println("ΜΟΤΕΡ 1 ON αριστερα" + String(flag));
        digitalWrite(stepPin, HIGH);
        digitalWrite(stepPin, LOW);
        digitalWrite(stepPin_R, HIGH);
        digitalWrite(stepPin_R, LOW);
         ret2 = myVR.recognize(buf, 50);
      
         Serial.println("ret2=" + String(ret2));
          
          if (ret2>0 and buf[1]>3){
           flag=1;
           Serial.println("****************************************************");
          }
       
              
        distance1 = sensor1.getDistance();
        distance2 = sensor2.getDistance();
        }
        
        break;
    }
        case st:
        
        Serial.println("stamatao");
        Serial.println(ret);
        Serial.println(buf[1]);
        Serial.println(myVR.recognize(buf, 50));
        break;
      default:
        Serial.println("Record function undefined");
        break;
    }
   
  }
}
